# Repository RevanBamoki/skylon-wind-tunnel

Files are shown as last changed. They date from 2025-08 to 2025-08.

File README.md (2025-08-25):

# Skylon V1: Open-Source Desktop Wind Tunnel

TunnelPhoto

  
  
  
[]()

A compact, 3D-printed wind tunnel you can build for classrooms, hobby and university labs.

---

## Repository Structure

- **STL/** - 3D-printable parts + print order & PLA settings  
- **CAD/** - Fusion 360 source (`.f3z`) and STEP export  
- **Electronics/** - Arduino firmware for dual BMP180 sensors (Uno + Nano)  
- **Software/** - Python live dashboard 
- **Docs/** - Assembly guide, and testing procedures  
- **BOM/** - Bill of Materials  

---

## Quick Start

1. Print parts per **STL/README.md**.  
2. Assemble per **Docs/assembly-guide.md**.  
3. Flash **Electronics/Firmware/** to:  
   - Uno → pressure P1, temperature T1  
   - Nano → pressure P2, temperature T2  
4. Per the steps in **Docs\testing-procedures.md**, run **Software/Python/bmp180_logger.py** (see its README for dependencies). 
5. Visualize flow. Data are *indicative only* (prototype, uncalibrated).  

---

## License & Disclaimer

- Licensed under the **MIT License**.  
- **Prototype status:** Results are for educational/demo purposes only.  

---

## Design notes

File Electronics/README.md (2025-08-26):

# Electronics - Firmware

Contains Arduino sketches for the **Skylon V1** wind tunnel.

---

## Boards

- **Arduino_Uno** → Handles BMP180 sensor for **P1** (pressure) and **T1** (temperature)  
- **Arduino_Nano** → Handles BMP180 sensor for **P2** (pressure) and **T2** (temperature)  

---

## Folder Structure

- **Firmware/Arduino_Uno/** → Code for Uno board  
- **Firmware/Arduino_Nano/** → Code for Nano board  

Each folder includes a sketch (`.ino`) that can be opened directly in the Arduino IDE.  

---

## Wiring

For both Uno and Nano:

- **BMP180 VCC → 5V**  
- **BMP180 GND → GND**  
- **BMP180 SDA → A4**  
- **BMP180 SCL → A5**  

---

## Libraries

Install via **Arduino IDE Library Manager**:

- **Adafruit BMP085 Library** (automatically pulls **Adafruit BusIO** and **Adafruit Unified Sensor**)  
- **Wire** (built-in)

---

## Uploading

1. Connect board via USB.  
2. Select the correct **board type** (Uno or Nano) and **COM port** in Arduino IDE.  
3. Open the corresponding sketch and click **Upload**.  
4. Close the Arduino IDE’s Serial Monitor before running the Python dashboard.

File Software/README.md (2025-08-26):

# Software — Live Dashboard & Logger

Python tools to visualize and log data from the dual-BMP180 sensor setup inside the wind tunnel.

---

## Overview
This package connects to two Arduino boards:

- **Arduino Uno** → T1 (temperature) + P1 (pressure)  
- **Arduino Nano** → T2 (temperature) + P2 (pressure)

The Arduino sketches are included in [`Electronics/Firmware`](../Electronics).

After flashing the boards, close the Arduino IDE’s serial monitor and run the Python program.

---

## Requirements

- **Python**: 3.8 or newer  
- Install dependencies with:  
  ```bash
  pip install -r requirements.txt
  ```
- `requirements.txt` includes:
  ```bash
  pyserial
  numpy
  matplotlib
  pandas

  ```

---

## Usage

1. Upload the Arduino sketches (`Arduino_Uno` and `Arduino_Nano`) to their respective boards.  
2. Close the Arduino IDE’s serial monitor so the ports are free.  
3. Edit the top of `bmp180_logger.py` if needed:  
   ```python
   UNO_PORT   = "COM5"     # or /dev/ttyUSB0
   NANO_PORT  = "COM4"     # or /dev/ttyUSB1
   CSV_FILE   = "bmp_dual_log.csv"
   LOG_TO_CSV = True       # set False to disable logging
   ```
4. Run the script:  
   ```bash
   python bmp180_logger.py
   ```
5. Four plots will appear and update live. If enabled, data will also be saved to CSV.  

---

## Example Output

- **Temperature plot**: T1 (Uno) vs T2 (Nano)  
- **Pressure plot**: P1 vs P2  
- **ΔP / U / E_loss plot**: flow dynamics  
- **Reynolds number plot**: flow regime indicator  

PythonExampleOutput

---

## Notes

- Sampling frequency is set to **20 Hz** (`SAMPLE_HZ`).  

- Plots auto-rescale but can be tuned (`HISTORY_SAMPLES`, `XTICK_SPACING_S`).

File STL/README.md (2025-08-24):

# STL Parts — Print Order

To build **Skylon V1**, print in roughly this order:

1. `bellmouth-1.stl`  
2. `bellmouth-2.stl`  
3. `bellmouth-3.stl`  
4. `test-section.stl`  
5. `magnet-lid.stl`  
6. `laser-holder-bottom.stl`  
7. `laser-holder-top.stl`  
8. `motor-case.stl`  
9. `motor-shaft-adapter.stl`  
10. `fan-turbine.stl`  
11. `exit-diffuser.stl`  
12. `tunnel-support-1.stl`  
13. `tunnel-support-2.stl`  
14. `incense-holder.stl`  

---

## Printing Guidelines (PLA)

- **General:** 0.2 mm layer height, 2 walls  
- **Structural parts** (bellmouth, test-section, tunnel supports, exit diffuser): **10% infill**  
- **Holders** (laser-holders, magnet-lid, incense-holder): **15% infill**  
- **Fan turbine & motor shaft adapter:** **100% infill** for strength  
- **Motor case:** **30% infill**
- **Slicer Used:** PrusaSlicer
- **3D Printers Used:** Prusa i3 MK3s+ and Creality Ender-3

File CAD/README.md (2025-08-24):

# CAD Files

- **Source/SkylonV1.f3z** – Fusion 360 native file  
  *(Due to size limits, available via Google Drive link provided here: https://drive.google.com/drive/folders/1G8i2QbCRmE-A4HHafTvrZ962FSSabpD7?usp=sharing)*

- **STEP.zip** – Contains the STEP export (`SkylonV1.step`) for cross-CAD use

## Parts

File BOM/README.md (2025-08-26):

# Bill of Materials (BOM)

List of required components for building **Skylon V1** wind tunnel.  

---

## Components

| Item                                    | Qty   | Notes                                                                 | Purchase Link | Est. price (USD) |
|-----------------------------------------|-------|----------------------------------------------------------------------|---------------|------------------|
| Arduino Uno R3                          | 1     | Compatible microcontroller board                                     | [Amazon – Uno R3](https://www.amazon.com/WWZMDiB-ATmega328P-microcontroller-Development-Compatible/dp/B0BV9XFQ5T/) | $6.99 |
| Arduino Nano V3.0 (ATmega328P)          | 1     | Compact microcontroller board                                        | [Amazon – Nano V3.0 (2-pack)](https://www.amazon.com/LUIRSAY-2Pcs-ATmega328P-Microcontroller-Compatible/dp/B0F1FQMNXM/) | $9.99 (2 pcs) |
| BMP180 Barometric Sensor Module         | 2     | I²C pressure/temperature breakout                                    | [Amazon – BMP180 (6-pack)](https://www.amazon.com/ACEIRMC-Temperature-Barometric-Pressure-Arduino/dp/B091GWXM8D/) | $6.99 (6 pcs) |
| RS-385 12 V Brushed DC Motor            | 1     | Suction blower motor; users may adapt CAD for motor case/shaft size  | [AliExpress – RS385 Motor](https://www.aliexpress.com/i/2251832829763932.html) | $2.03 |
| 532 nm Green Laser Pointer              | 1     | Forms laser sheet with prism                                         | [Amazon – Green Laser Pointer](https://www.amazon.com/Advanced-Long-Range-Laser-Pointer-Power/dp/B0DP9G71M2/) | $8.53 |
| BK7 Triangular Glass Prism (25 mm base) | 1     | Fanning laser into sheet; adjust CAD holder to prism height          | [eBay – BK7 Triangular Prism](https://www.ebay.com/itm/304094073131) | $7.51 |
| Rectangular Neodymium Magnets (20×6×1.5 mm, N42) | 8 | For test section lid; replace CAD slot sizes as needed | [First4Magnets – 20×6×1.5 mm](https://www.first4magnets.com/product/20-x-6-x-15mm-thick-n42-neodymium-magnet-16kg-pull-19331) | ~ £5.19 / pack |
| PLA Filament (1.75 mm, 1 kg spool)      | ~1    | For all 3D-printed parts                                             | [Amazon – Overture PLA](https://www.amazon.com/OVERTURE-Filament-Consumables-Dimensional-Accuracy/dp/B07PGY2JP1/) | $14.99 |
| Acrylic Sheet, clear 6 mm               | 1     | Window; order ≥90×90 mm and cut to size                             | [Sheet Plastics – 6 mm Clear](https://www.sheetplastics.co.uk/clear-acrylic/6mm-clear-acrylic-sheet-cut-to-size#/) | ~ £1–2 (size-dependent) |
| Incense Sticks                          | –     | For smoke visualization of airflow                                   | [Amazon – HEM Incense (120 pcs)](https://www.amazon.com/Hem-Lavender-Incense-Sticks-Count/dp/B0021GBNPC/) | $6.90 |
| Adjustable DC Bench Supply (0–30 V, 5 A)| 1     | For motor speed control; crocodile clips included                    | [Amazon – WEP DC Power Supply](https://www.amazon.com/Adjustable-Switching-Regulated-Precision-Adjustments/dp/B0BN1F6CGZ/) | $49.99 |

---

**Estimated prototype total:** **~$155–165** (parts only; varies by supplier and shipping).  

### Notes
- The **motor** is RS-385-class brushed DC; other small brushed DC motors can be used if the CAD is adapted for case/shaft size.  
- The **magnets** in my prototype were **oval (obround) slot magnets**, but these are not ideal and hard to source. Rectangular magnets (like the First4Magnets link) are better and more readily available. You can edit the CAD slot dimensions to match whatever magnet size you purchase (smaller sizes are fine).  
- The **BK7 prism** (25 mm × ~80 mm) matches your build, but any equilateral prism works if you adjust the holder CAD.  
- Acrylic sheet is cut-to-size; just ensure at least 90 × 90 mm and trim if needed. Or if you want a smaller size than the one I used, just make sure to update the test section rectangular.  
- **Microcontrollers:** You don’t strictly need both an Uno and a Nano. You could use two Unos or two Nanos - sensor performance isn’t affected. The reason for two boards is that the BMP180 sensors both use the same fixed I²C address (0x77), so a single microcontroller cannot distinguish them on the same bus. Splitting them across two boards is the simplest solution.  
- Buying multipacks (Nano, BMP180) reduces cost but leaves spares for contributors.

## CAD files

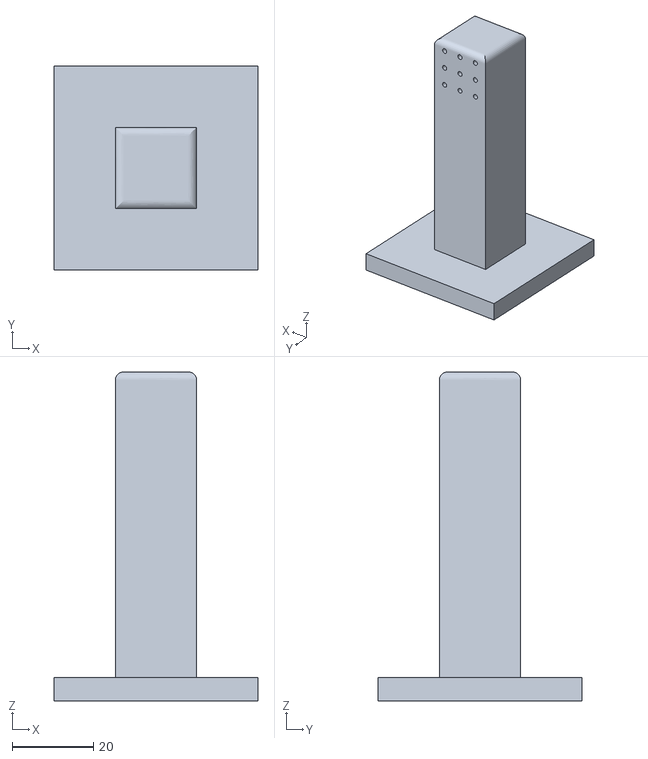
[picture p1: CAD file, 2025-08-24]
STL/STL Files/incense-holder.stl
50.0 x 50.0 x 80.8

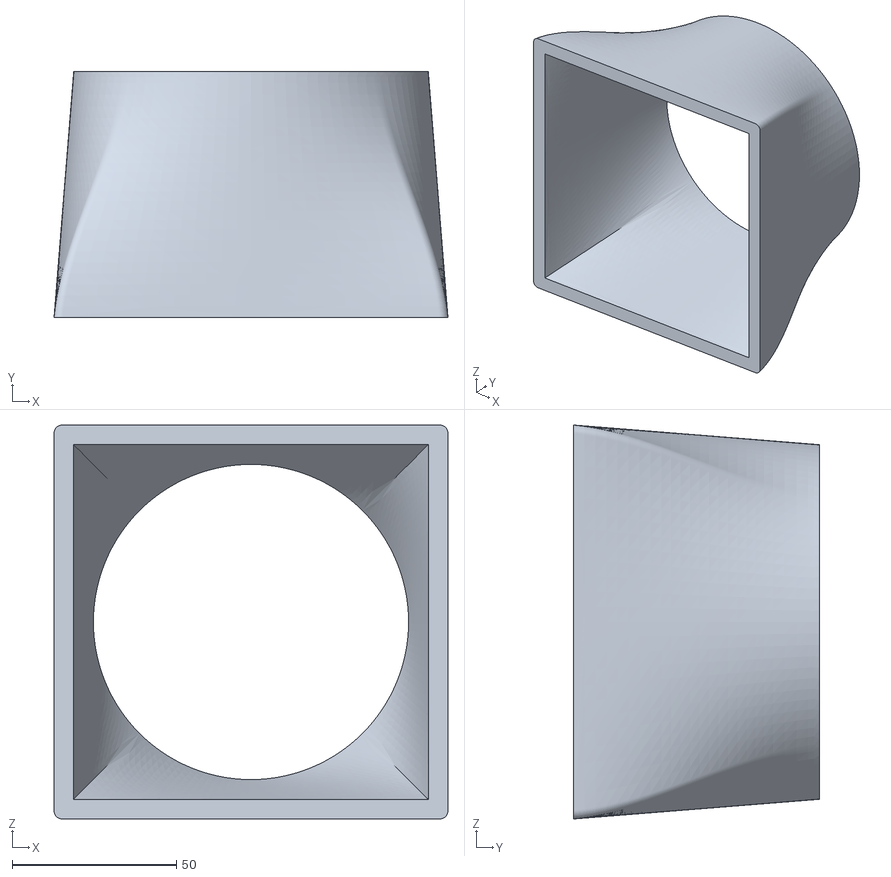
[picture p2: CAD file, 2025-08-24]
STL/STL Files/exit-diffuser.stl
120.0 x 75.0 x 120.0

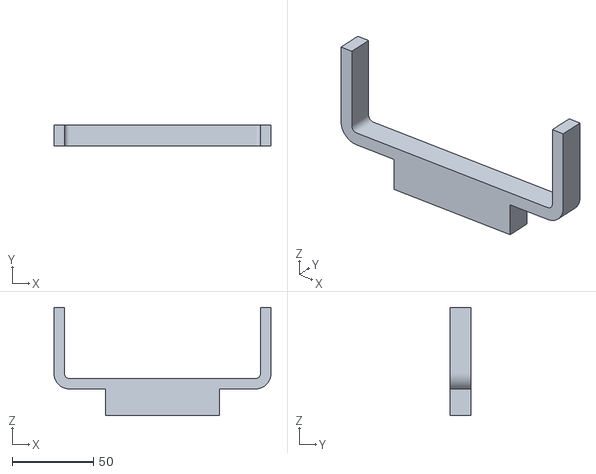
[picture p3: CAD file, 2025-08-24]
STL/STL Files/tunnel-support-2.stl
133.8 x 13.0 x 66.6

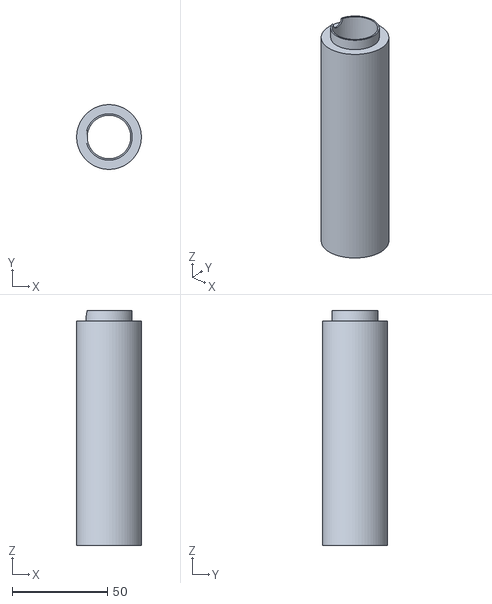
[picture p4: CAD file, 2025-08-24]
STL/STL Files/laser-holder-bottom.stl
34.0 x 34.0 x 123.4

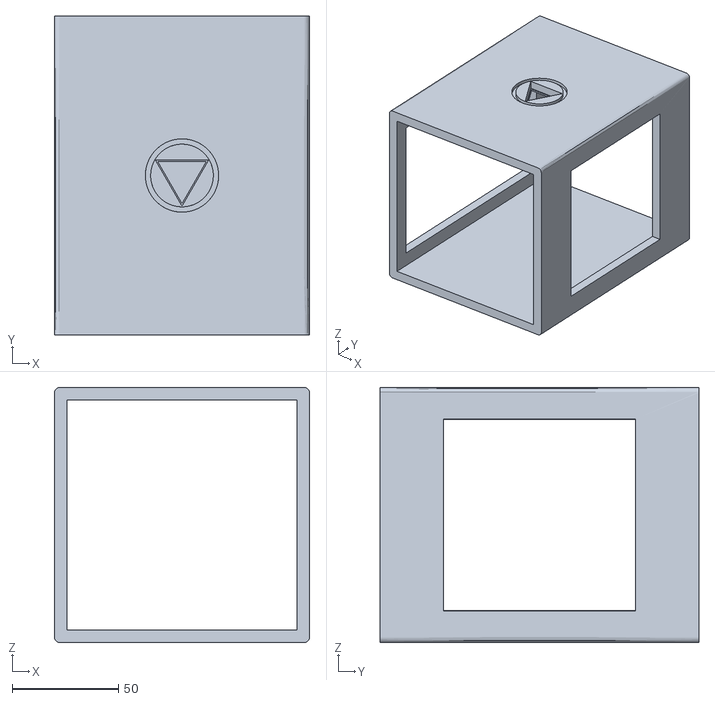
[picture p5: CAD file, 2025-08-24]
STL/STL Files/test-section.stl
120.0 x 150.0 x 120.0

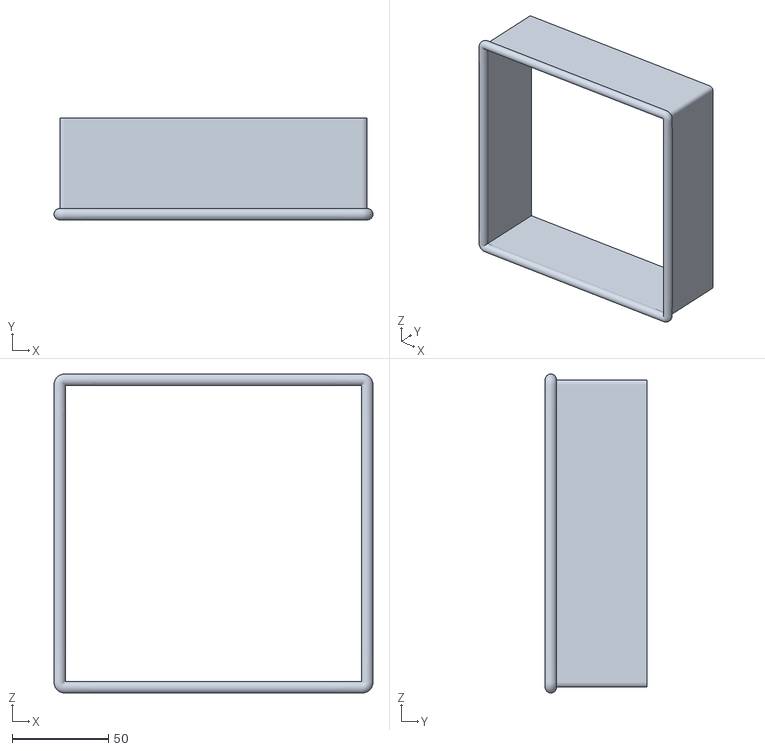
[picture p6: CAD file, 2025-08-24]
STL/STL Files/bellmouth-1.stl
166.0 x 53.0 x 166.0

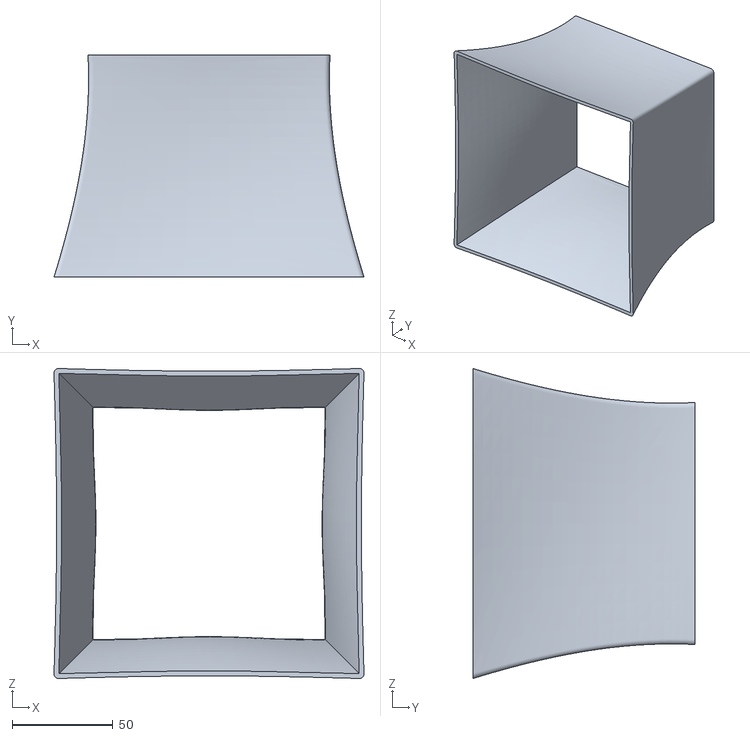
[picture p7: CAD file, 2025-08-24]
STL/STL Files/bellmouth-3.stl
153.6 x 110.0 x 153.6

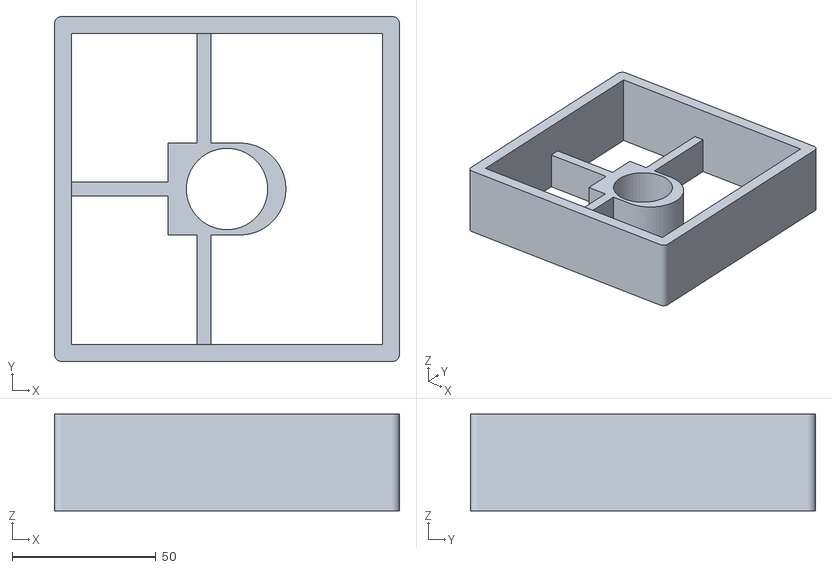
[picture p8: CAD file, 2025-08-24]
STL/STL Files/motor-case.stl
120.0 x 120.0 x 33.6

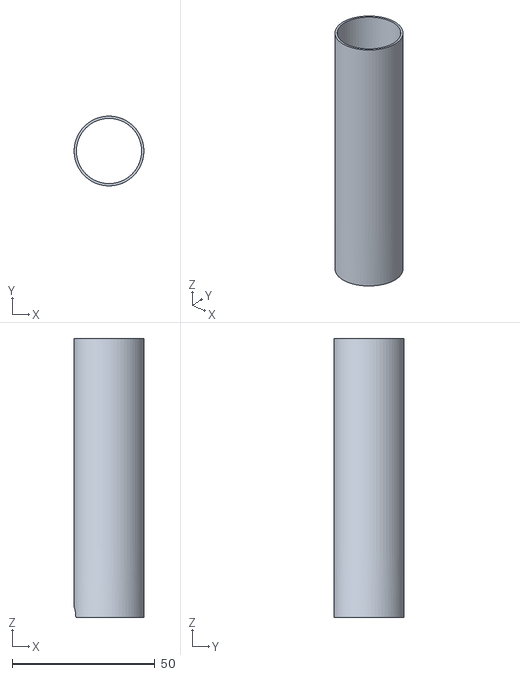
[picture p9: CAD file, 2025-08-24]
STL/STL Files/laser-holder-top.stl
24.4 x 24.4 x 97.6

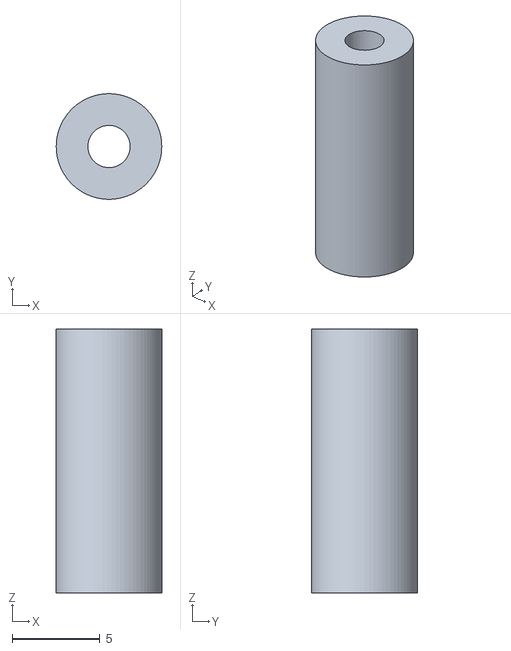
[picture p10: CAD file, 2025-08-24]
STL/STL Files/motor-shaft-adapter.stl
6.00 x 5.99 x 15.0

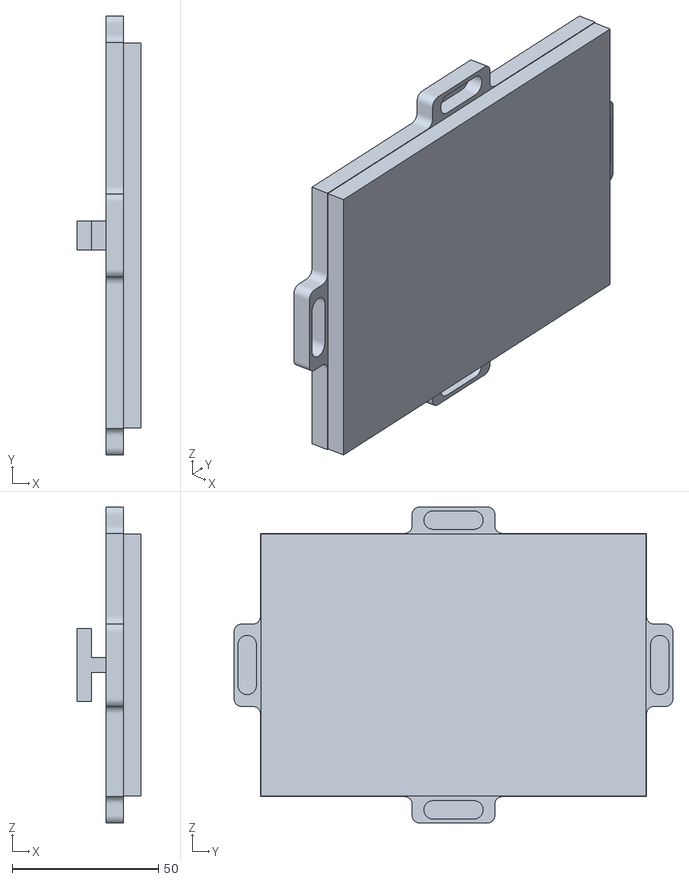
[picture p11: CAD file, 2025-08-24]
STL/STL Files/magnet-lid.stl
22.0 x 150.0 x 108.0

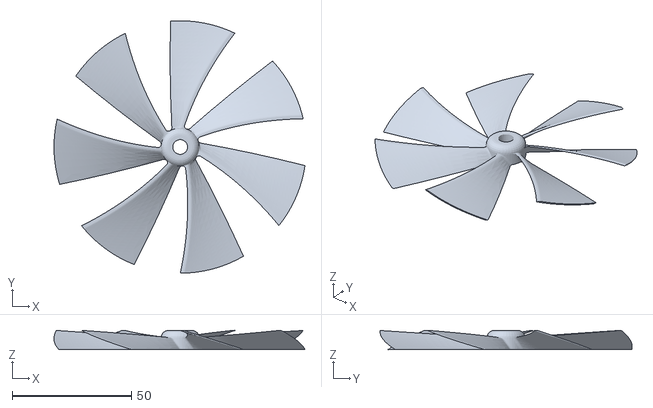
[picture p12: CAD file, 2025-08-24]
STL/STL Files/fan-turbine.stl
105.4 x 106.0 x 8.00

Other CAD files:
STL/STL Files/tunnel-support-1.stl

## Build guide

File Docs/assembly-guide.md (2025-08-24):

# Skylon V1 – Assembly Guide

Instructions for assembling the **Skylon V1 desktop wind tunnel**.

---

## 1. Adhesives and General Notes

- PLA parts are joined using **superglue with activator spray**.  
- Before gluing, **dry-fit all parts** to ensure proper alignment.  
- For parts that include magnets, carefully **check polarity before securing** (see Section 3).  
- This V1 prototype was built quickly and simply. Some shortcuts (like gluing the motor) are not recommended for long-term reliability but are documented here for transparency.  

---

## 2. Structural Assembly

1. Print and prepare all STL parts (see [STL/README.md](../STL) for recommended print order).  
2. Bond the tunnel parts in sequence:  
   - **Bellmouth sections → Test section → Exit diffuser → Tunnel Supports**  
3. Ensure all joints are square and aligned to avoid air leakage.  

---

## 3. Magnet Installation (Critical Step)

- **Magnets required:** 8 total  
  - 4 in the **test section**  
  - 4 in the **magnet lid**  
- Place magnets into their slots.  
- **Check polarity before gluing**: magnets must attract, not repel.  
- Once polarity is correct, secure with superglue.  

**Warning:** If glued incorrectly, parts cannot be salvaged; you will need to reprint.  

---

## 4. Motor and Turbine

- Motor sits inside the **3D-printed motor case**.  
- For V1, the motor was **superglued** into the case (fasteners not included).  
- Attach the turbine to the motor shaft:  
  - In V1, a **custom 3D-printed adapter** was used to connect the motor shaft and turbine.  
  - Design your own adapter depending on your motor type.  
- Wires with crocodile clips connect to the motor leads and exit through the diffuser section and connect to a **DC power supply**.  

**Note:** A standalone DC motor with custom turbine was chosen instead of a PC fan, since suitable fans were more expensive and provided weaker suction.  

---

## 5. Laser & Flow Visualization

- A **green laser pointer** was used.  
- Since the beam does not naturally scatter, a **triangular prism** was glued in place to create a **laser sheet**.  
- The laser sheet illuminates smoke from incense sticks in the test section, allowing laminar/turbulent visualization.  

---

## 6. Smoke Source

- **Incense sticks** are used for smoke generation.  
- Place a **wet paper towel** beneath the sticks to catch falling ash and prevent surface damage.  

---

## 7. Sensor Installation

- Two **BMP180 pressure/temperature sensors** were mounted beneath the tunnel.
- Slots for sensors were manually drilled into the bottom of the PLA (However, if you take dimensions and incorporate holes in your design, it's way more convenient). 
  - Ensure enough clearance for the modules and their 4-wire connections.  
  - A **rectangular slot** is recommended.  
- Sensors connect to Arduino boards as described in [Electronics/Firmware](../Electronics).  

---

## 8. Power & Wiring

- Motor connected to an **external DC power supply**.  
- Sensors wired to **Arduino Nano & Uno** (see [Electronics/Firmware](../Electronics)), which connect to a laptop via USB.  
- Data is logged and processed using the Python script in [Software/Python/bmp180_logger.py](../Software).  

---

## 9. Final Notes

- This V1 prototype is a **proof of concept**, not optimized for durability or production.  
- Future versions should:  
  - Replace glued joints with **screws/fasteners**  
  - Add **dedicated sensor mounts**  
  - Redesign the motor housing for easier serviceability  
- Despite its limitations, this prototype is functional and capable of producing meaningful airflow visualization.

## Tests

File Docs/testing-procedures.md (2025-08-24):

# Testing Procedures (Skylon V1 - Prototype)

Procedures for verifying assembly, sensor operation, and visualization on the **Skylon V1 desktop wind tunnel**.

---

## 1. Leak & Fit Check

- Feel for leaks around glue joints.  
- Re-glue if any clear leaks are detected.  

---

## 2. Sensor Check (Room Conditions)

- Power each Arduino via USB.  
- Open Serial Monitor (9600 baud) **one at a time**.  
- Confirm readings:  
  - **T1/T2** ≈ room temperature  
  - **P1/P2** ≈ ambient (≈100–103 kPa)  
- Close Serial Monitor when finished.  

---

## 3. Dual-Stream Readout

- Run:  
  ```bash
  python Software/Python/bmp180_logger.py
  ```  
  (with the correct `UNO_PORT` and `NANO_PORT` set in the script).  
- You should see live plots for:  
  - T1, T2  
  - P1, P2  
  - ΔP  
  - U (airflow velocity)  
  - E_loss  
  - Re (Reynolds number)  
- **Note:** Reynolds number values are *indicative only* (prototype, uncalibrated).  

---

## 4. Flow Visualization

- Place incense upstream.  
- Turn on the **laser + prism** to form a sheet.  
- Observe flow patterns at the model.  

---

## 5. Data Logging

- Enable logging by setting:  
  ```python
  LOG_TO_CSV = True
  ```  
- Inspect results in:  
  ```
  bmp_dual_log.csv
  ```  

---

## Safety

- **Laser:** Avoid direct or reflective eye exposure. Always use protective eyewear.  
- **Incense:** Ensure good ventilation. Place a damp paper towel beneath sticks to catch ash.  
- **Hot components/adhesives:** Handle with care during extended operation.

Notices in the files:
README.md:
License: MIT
